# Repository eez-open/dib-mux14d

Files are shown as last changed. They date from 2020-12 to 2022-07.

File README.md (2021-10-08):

### Ownership and License
The contributors are listed in CONTRIB.TXT.

Licenses | OSHWA UID
--|--
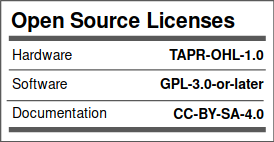
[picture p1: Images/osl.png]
osl
 | OSHW-HR000010 (https://certification.oshwa.org/hr000010.html)

### Overview

The EEZ DIB MUX14D module features two 7:1 reed relay 2-wire multiplexer that can be connect together to make single 14:1 multiplexer. 

### Feature list

* On-board STM32F030C6T6 or STM32F031C4T6 MCU 
* 2 x 16-pin dual row 3.81 mm connectors
* 2 x ADIB connectors (10-pin 2 mm), ADIB ID=002
* Dual 2-wire 7:1 reed relay 2-line multiplexer 
* On-board +3.3 V LDO
* Firmware download via UART
* Optional SWD for debugging
* I2C EEPROM for storing board specific parameters
* Dimensions: 131 x 95 mm, 2-layer PCB

### r1B2 prototype

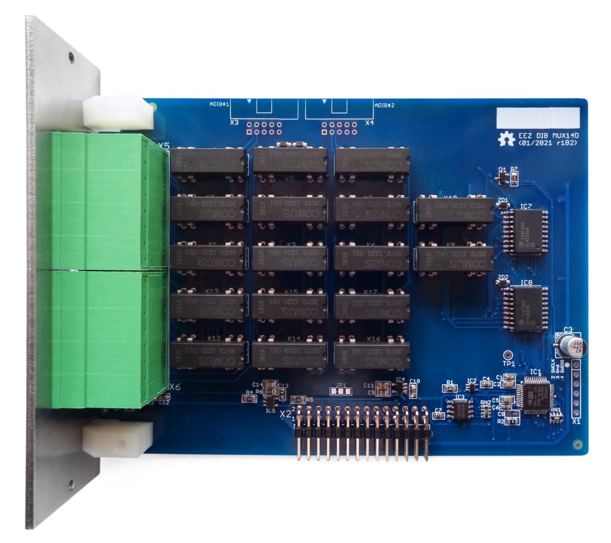
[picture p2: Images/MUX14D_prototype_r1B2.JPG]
prototype


### Firmware repository

https://github.com/eez-open/dib-mux14d-fw  
The firmware download procedure is described in [Chapter 13.2]((https://www.envox.eu/eez-bench-box-3/bb3-user-manual/13-firmware-upgrade/#bb3_man_module_upgrade) of the User Manual.

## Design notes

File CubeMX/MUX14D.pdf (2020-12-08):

## MUX14D Project Configuration Report

# 1. Description

## 1.1. Project

Project Name | MUX14D
Board Name | custom
Generated with: | STM32CubeMX 5.6.1
Date | 12/07/2020

## 1.2. MCU

MCU Series | STM32F0
MCU Line | STM32F0x0 Value Line
MCU name | STM32F030C6Tx
MCU Package | LQFP48
MCU Pin number | 48

# 2. Pinout Configuration

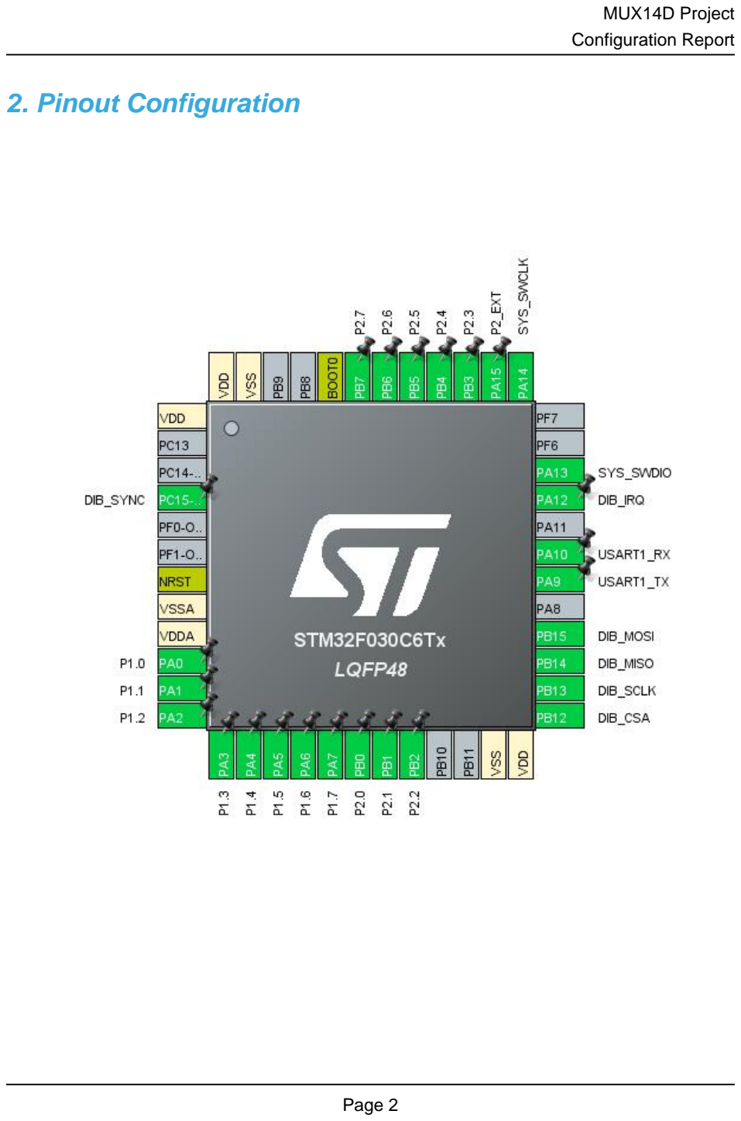
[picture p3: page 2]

# 3. Pins Configuration

Pin Number LQFP48 | Pin Name (function after reset) | Pin Type | Alternate Function(s) | Label
1 | VDD | Power
4 | PC15-OSC32_OUT * | I/O | GPIO_Input | DIB_SYNC
7 | NRST | Reset
8 | VSSA | Power
9 | VDDA | Power
10 | PA0 * | I/O | GPIO_Output | P1.0
11 | PA1 * | I/O | GPIO_Output | P1.1
12 | PA2 * | I/O | GPIO_Output | P1.2
13 | PA3 * | I/O | GPIO_Output | P1.3
14 | PA4 * | I/O | GPIO_Output | P1.4
15 | PA5 * | I/O | GPIO_Output | P1.5
16 | PA6 * | I/O | GPIO_Output | P1.6
17 | PA7 * | I/O | GPIO_Output | P1.7
18 | PB0 * | I/O | GPIO_Output | P2.0
19 | PB1 * | I/O | GPIO_Output | P2.1
20 | PB2 * | I/O | GPIO_Output | P2.2
23 | VSS | Power
24 | VDD | Power
25 | PB12 | I/O | SPI1_NSS | DIB_CSA
26 | PB13 | I/O | SPI1_SCK | DIB_SCLK
27 | PB14 | I/O | SPI1_MISO | DIB_MISO
28 | PB15 | I/O | SPI1_MOSI | DIB_MOSI
30 | PA9 | I/O | USART1_TX
31 | PA10 | I/O | USART1_RX
33 | PA12 * | I/O | GPIO_Output | DIB_IRQ
34 | PA13 | I/O | SYS_SWDIO
37 | PA14 | I/O | SYS_SWCLK
38 | PA15 * | I/O | GPIO_Output | P2_EXT
39 | PB3 * | I/O | GPIO_Output | P2.3
40 | PB4 * | I/O | GPIO_Output | P2.4
41 | PB5 * | I/O | GPIO_Output | P2.5
42 | PB6 * | I/O | GPIO_Output | P2.6
43 | PB7 * | I/O | GPIO_Output | P2.7
44 | BOOT0 | Boot
47 | VSS | Power
48 | VDD | Power

## * The pin is affected with an I/O function

# 4. Clock Tree Configuration

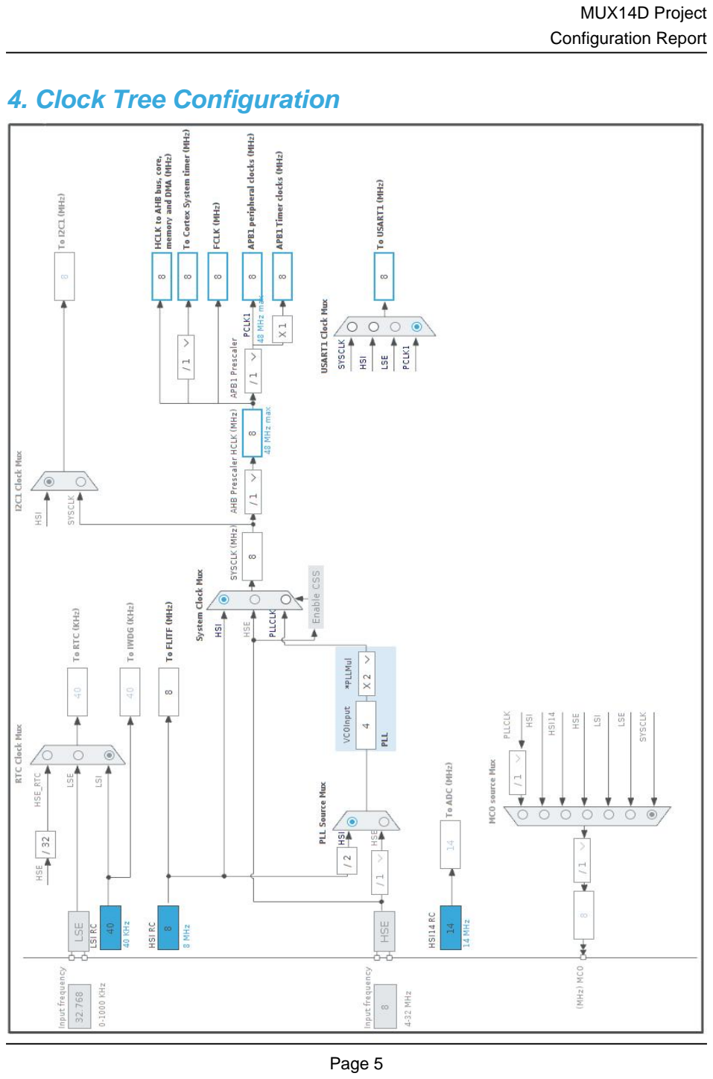
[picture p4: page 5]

# 5. Software Project

## 5.1. Project Settings

Name | Value
Project Name | MUX14D
Project Folder | /home/denis/BACKUP/EEZ/Digital control/MCU/STM32/Projects/MUX14D
Toolchain / IDE | EWARM V8.32
Firmware Package Name and Version | STM32Cube FW_F0 V1.11.0

## 5.2. Code Generation Settings

Name | Value
STM32Cube MCU packages and embedded software | Copy all used libraries into the project folder
Generate peripheral initialization as a pair of '.c/.h' files | No
Backup previously generated files when re-generating | No
Delete previously generated files when not re-generated | Yes
Set all free pins as analog (to optimize the power consumption) | No

# 6. Power Consumption Calculator report

### 6.1. Microcontroller Selection

Series | STM32F0
Line | STM32F0x0 Value Line
MCU | STM32F030C6Tx
Datasheet | 024849_Rev2

### 6.2. Parameter Selection

Temperature | 25
Vdd | 3.6

### 6.3. Battery Selection

Battery | Li-SOCL2(A3400)
Capacity | 3400.0 mAh
Self Discharge | 0.08 %/month
Nominal Voltage | 3.6 V
Max Cont Current | 100.0 mA
Max Pulse Current | 200.0 mA
Cells in series | 1
Cells in parallel | 1

## 6.4. Sequence

Step | Step1 | Step2
Mode | RUN | STOP
Vdd | 3.6 | 3.6
Voltage Source | Battery | Battery
Range | No Scale | No Scale
Fetch Type | FLASH | n/a
CPU Frequency | 48 MHz | 0 Hz
Clock Configuration | HSE PLL All IPs ON | Regulator_LP
Clock Source Frequency | 8 MHz | 0 Hz

### Peripherals

Additional Cons. | 0 mA | 0 mA
Average Current | 23.46 mA | 7.9 µA
Duration | 0.1 ms | 0.9 ms
DMIPS | 0.0 | 0.0
Ta Max | 100.36 | 105
Category | In DS Table | In DS Table

## 6.5. RESULTS

Sequence Time | 1 ms | Average Current | 2.35 mA
Battery Life | 1 month, 29 days, 16 hours | Average DMIPS | 0.0 DMIPS

## 6.6. Chart

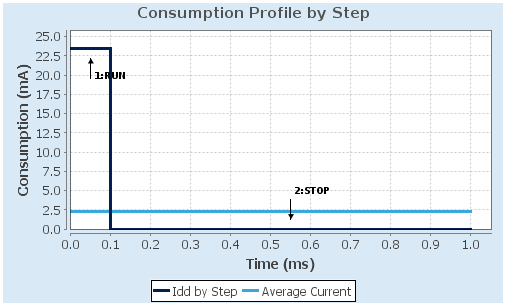
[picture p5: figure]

# 7. IPs and Middleware Configuration

# 7.1. CRC

## mode: Activated 7.1.1. Parameter Settings:

### Basic Parameters:

Default Polynomial State | Enable
Default Init Value State | Enable

### Advanced Parameters:

Input Data Inversion Mode | None
Output Data Inversion Mode | Disable
Input Data Format | Bytes

# 7.2. GPIO

# 7.3. SPI1

## Mode: Full-Duplex Slave Hardware NSS Signal: Hardware NSS Input Signal 7.3.1. Parameter Settings:

### Basic Parameters:

Frame Format | Motorola
Data Size | 4 Bits
First Bit | MSB First

### Clock Parameters:

Clock Polarity (CPOL) | Low
Clock Phase (CPHA) | 1 Edge

### Advanced Parameters:

CRC Calculation | Disabled
NSS Signal Type | Input Hardware

# 7.4. SYS

## mode: Debug Serial Wire Timebase Source: SysTick

# 7.5. USART1

## Mode: Asynchronous 7.5.1. Parameter Settings:

### Basic Parameters:

Baud Rate | 38400
Word Length | 8 Bits (including Parity)
Parity | None
Stop Bits | 1

### Advanced Parameters:

Data Direction | Receive and Transmit
Over Sampling | 16 Samples
Single Sample | Disable

### Advanced Features:

Auto Baudrate | Disable
TX Pin Active Level Inversion | Disable
RX Pin Active Level Inversion | Disable
Data Inversion | Disable
TX and RX Pins Swapping | Disable
Overrun | Enable
DMA on RX Error | Enable
MSB First | Disable

### * User modified value

# 8. System Configuration

# 8.1. GPIO configuration

IP | Pin | Signal | GPIO mode | GPIO pull/up pull down | Max Speed | User Label
SPI1 | PB12 | SPI1_NSS | Alternate Function Push Pull | No pull-up and no pull-down | High * | DIB_CSA
| PB13 | SPI1_SCK | Alternate Function Push Pull | No pull-up and no pull-down | High * | DIB_SCLK
| PB14 | SPI1_MISO | Alternate Function Push Pull | No pull-up and no pull-down | High * | DIB_MISO
| PB15 | SPI1_MOSI | Alternate Function Push Pull | No pull-up and no pull-down | High * | DIB_MOSI
SYS | PA13 | SYS_SWDIO | n/a | n/a | n/a
| PA14 | SYS_SWCLK | n/a | n/a | n/a
USART1 | PA9 | USART1_TX | Alternate Function Push Pull | No pull-up and no pull-down | High *
| PA10 | USART1_RX | Alternate Function Push Pull | No pull-up and no pull-down | High *
| OSC32_OU T | GPIO_Input | Input mode | No pull-up and no pull-down | n/a | DIB_SYNC
| PA0 | GPIO_Output | Output Push Pull | No pull-up and no pull-down | Low | P1.0
| PA1 | GPIO_Output | Output Push Pull | No pull-up and no pull-down | Low | P1.1
| PA2 | GPIO_Output | Output Push Pull | No pull-up and no pull-down | Low | P1.2
| PA3 | GPIO_Output | Output Push Pull | No pull-up and no pull-down | Low | P1.3
| PA4 | GPIO_Output | Output Push Pull | No pull-up and no pull-down | Low | P1.4
| PA5 | GPIO_Output | Output Push Pull | No pull-up and no pull-down | Low | P1.5
| PA6 | GPIO_Output | Output Push Pull | No pull-up and no pull-down | Low | P1.6
| PA7 | GPIO_Output | Output Push Pull | No pull-up and no pull-down | Low | P1.7
| PB0 | GPIO_Output | Output Push Pull | No pull-up and no pull-down | Low | P2.0
| PB1 | GPIO_Output | Output Push Pull | No pull-up and no pull-down | Low | P2.1
| PB2 | GPIO_Output | Output Push Pull | No pull-up and no pull-down | Low | P2.2
| PA12 | GPIO_Output | Output Push Pull | No pull-up and no pull-down | Low | DIB_IRQ
| PA15 | GPIO_Output | Output Push Pull | No pull-up and no pull-down | Low | P2_EXT
| PB3 | GPIO_Output | Output Push Pull | No pull-up and no pull-down | Low | P2.3
| PB4 | GPIO_Output | Output Push Pull | No pull-up and no pull-down | Low | P2.4
| PB5 | GPIO_Output | Output Push Pull | No pull-up and no pull-down | Low | P2.5
| PB6 | GPIO_Output | Output Push Pull | No pull-up and no pull-down | Low | P2.6
| PB7 | GPIO_Output | Output Push Pull | No pull-up and no pull-down | Low | P2.7
GPIO | PC15-

# 8.2. DMA configuration

DMA request | Stream | Direction | Priority
SPI1_RX | DMA1_Channel2 | Peripheral To Memory | Low
SPI1_TX | DMA1_Channel3 | Memory To Peripheral | Low

## SPI1_RX: DMA1_Channel2 DMA request Settings:

Mode: | Normal
Peripheral Increment: | Disable
Memory Increment: | Enable *
Peripheral Data Width: | Byte
Memory Data Width: | Byte

## SPI1_TX: DMA1_Channel3 DMA request Settings:

Mode: | Normal
Peripheral Increment: | Disable
Memory Increment: | Enable *
Peripheral Data Width: | Byte
Memory Data Width: | Byte

# 8.3. NVIC configuration

Interrupt Table | Enable | Preenmption Priority | SubPriority
Non maskable interrupt | true | 0 | 0
Hard fault interrupt | true | 0 | 0
System service call via SWI instruction | true | 0 | 0
Pendable request for system service | true | 0 | 0
System tick timer | true | 0 | 0
DMA1 channel 2 and 3 interrupts | true | 0 | 0
Flash global interrupt | unused
RCC global interrupt | unused
SPI1 global interrupt | unused
USART1 global interrupt | unused

### * User modified value

# 9. Predefined Views - Category view : Current

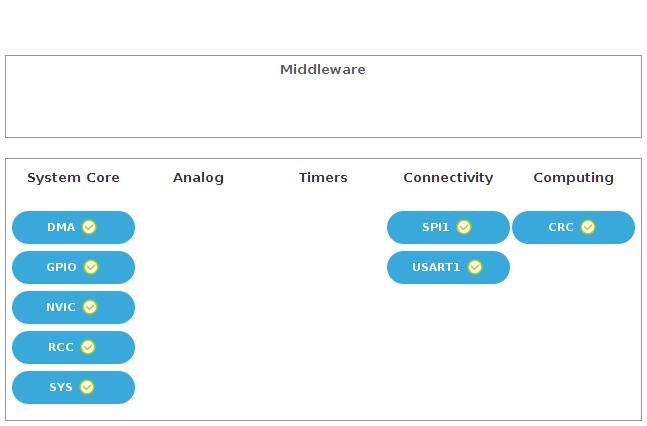
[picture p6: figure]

# 10. Software Pack Report

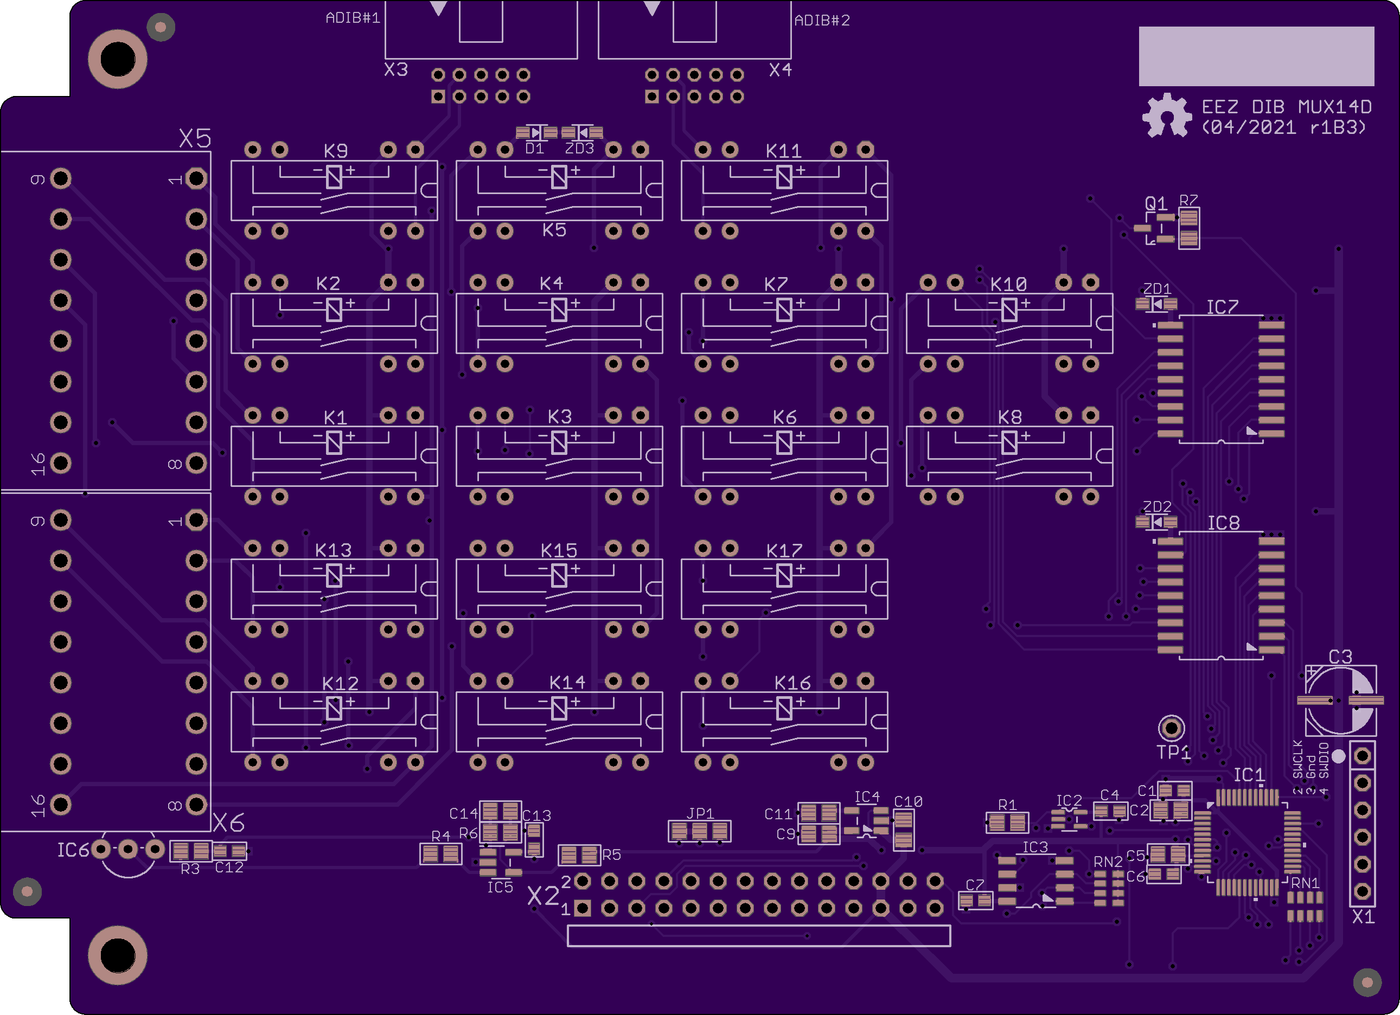
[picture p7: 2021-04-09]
Images/EEZ_DIB_MUX14D_PCB_top.png

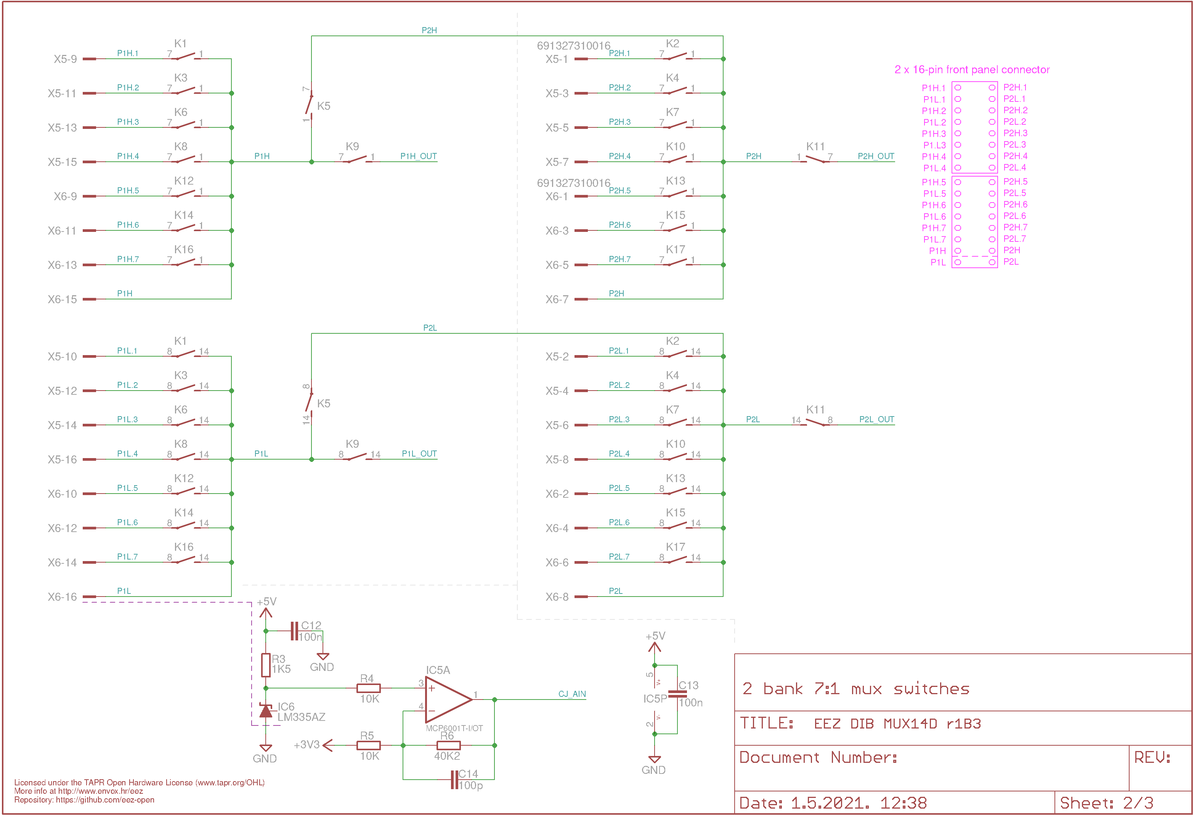
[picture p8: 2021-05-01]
EEZ DIB MUX14D r1B3 Sheet2of3.png

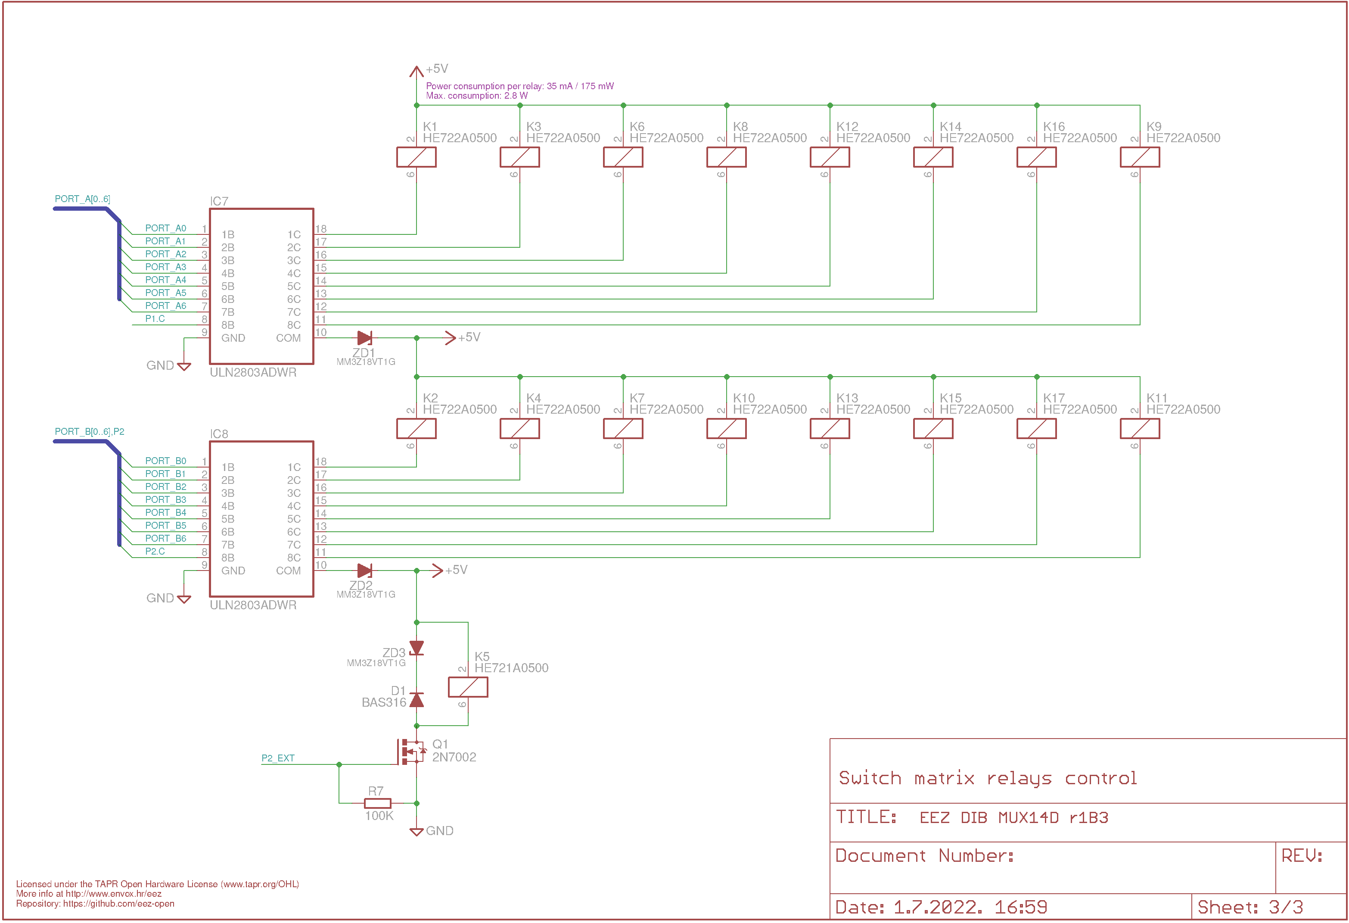
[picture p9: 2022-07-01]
EEZ DIB MUX14D r1B3 Sheet3of3.png

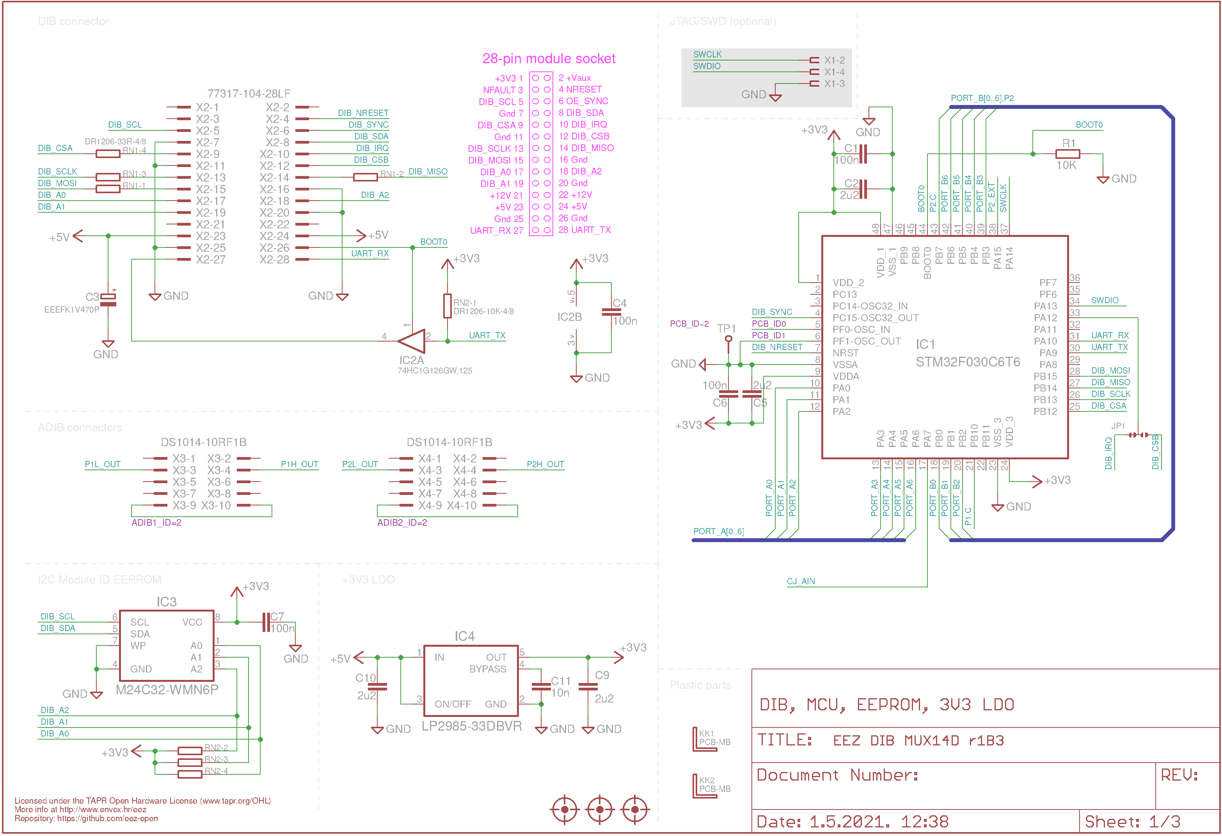
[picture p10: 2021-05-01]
EEZ DIB MUX14D r1B3 Sheet1of3.png

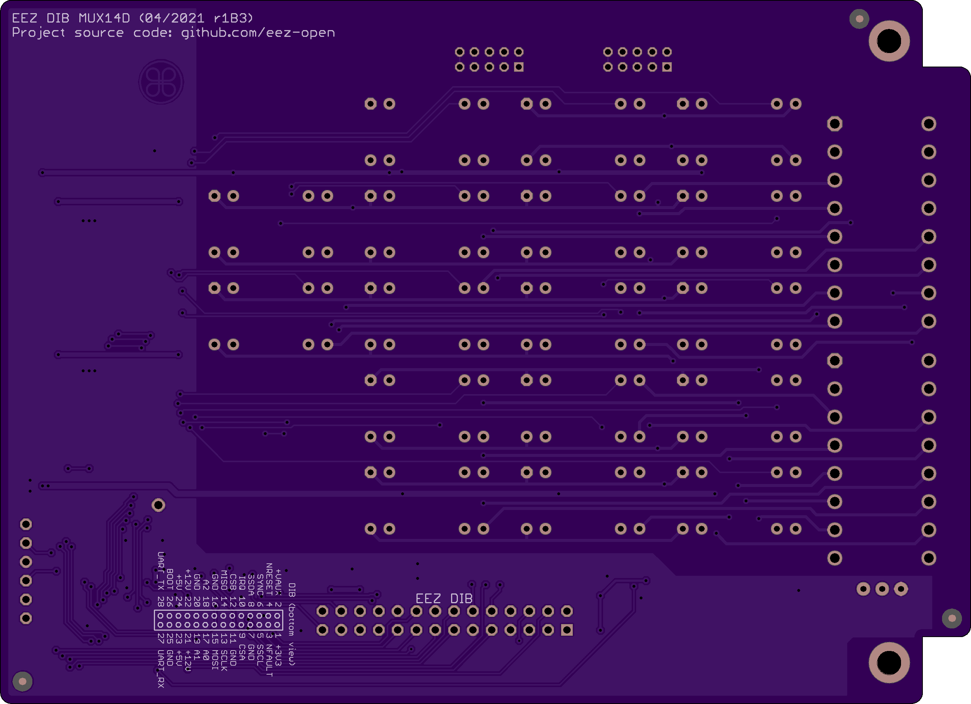
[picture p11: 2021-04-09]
Images/EEZ_DIB_MUX14D_PCB_bottom.png

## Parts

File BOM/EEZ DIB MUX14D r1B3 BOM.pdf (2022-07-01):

EEZ DIB MUX14D BOM (r1B3, 2022-07-01) Project source code at https://github.com/eez-open/dib-prel6
Farnell / Element14 # Unit price Qty Part name Package Reference designator Code Part Number MOQ € | Digi-Key Unit price Part Number MOQ € | Mouser Unit price Part Number MOQ €
| | 80-C0603C104M4R
VJ0805Y103JXXP W1BC | | 710-885012207122
| | 80-C0805C101K5G
C2, C5, C9, C10 GRM21BR71C225 KA12L | | 80-C0805C225M4R ECLR
| | 667-EEE-FK1V470P
1 | 6 100n | 0603 | 2522597 | 0,011 10 | 490-4774-1-ND | 0,029 100 | 0,007 100
2 | 1 10n | 0805 | C11 | 2896555 | 0,065 10 | 490-7194-1-ND | 0,017 | 10 | 0,036 10
3 | 1 100p | C0G, 0805 | C14 | 2896861 | 0,023 10 | 399-15000-1-ND | 0,019 | 10 | 0,032 10
4 | 4 2u2 | 0805 | 1828829 | 0,198 | 5 | 1276-2954-1-ND | 0,085 | 10 | 0,078 10
5 | 1 EEEFK1V470P | C3 | 9695850 | EEEFK1V470P | 0,344 | 1 | PCE3842CT-ND | 0,312 | 10 | 0,238 10
6 | 1 BAS316 | SOD-323 | D1 | 8734275 | BAS316,115 | 0,193 | 5 | 1727-7370-1-ND | 0,120 | 1 | 771-BAS316-T/R | 0,179 | 1
7 | 1 STM32F030C6T6 | LQFP-48 | IC1 | 2393632 | STM32F030C6T6 | 1,350 | 1 | | 1,360 | 1 | | 1,360 | 1
8 | 1 74HC1G126GW.125 | TSSOP-5 | IC2 | - | | | | 1727-6037-1-ND | 0,360 | 1 | 0,369 | 1
9 | 1 M24C32-WMN6P | SOIC-8 | IC3 | 1224413 | M24C32-WMN6P | 0,212 | 5 | - | | | 0,210 | 1
10 | 1 | SOT-23-5 | IC4 | 1053660 | | 0,610 | 1 | 296-18476-1-ND | 0,540 | 1 | 0,507 | 1
11 | 1 | SOT-23-5 | IC5 | 4974992 | MCP6001T-I/OT | 0,219 | 1 | | 0,200 | 1 | 0,203 | 1
12 | 1 LM335AZ | | IC6 | 1564358 | LM335AZ | 1,780 | 1 | | 1,760 | 1 | 1,740 | 1
13 | 2 ULN2803ADWR | SOIC-18 | IC7, IC8 | 3125103 | ULN2803ADWR | 1,120 | 5 | 296-15777-1-ND | 1,090 | 1 | 1,090 | 1
14 | 17 HE722A0500 | - | HE722A0500 | 4,323 | 10 | 4,300 10
15 | 1 2N7002 | SOT-23 | Q1 | 1713825 | 2N7002K-7 | 0,148 | 5 | 0,126 | 10 | 0,113 10
16 | 3 10K | 0805 | R1, R4, R5 | 9237755 | 0,022 10 | 0,039 | 10 | 0,014 10
17 | 1 1K5 | 0805 | R3 | 2447592 | 0,009 10 | A129751CT-ND | 0,041 | 10 | 0,041 10
18 | 1 40K2 | 0805 | R6 | 2447658 | 0,009 10 | 0,055 | 10 | 0,035 10
19 | 1 100K | 0805 | R7 | 2447551 | 0,010 10 | 0,024 | 10 | 0,040 10
20 | 1 DR1206-33R-4/8 | 1206 resistor array | RN1 | 1770128 | CAY16-330J4LF | 0,069 10 | 0,090 | 1 | 0,085 | 1
21 | 1 DR1206-10K-4/8 | 1206 resistor array | RN2 | 1770137 | CAY16-103J4LF | 0,031 10 | 0,058 | 10 | 0,021 10
C1, C4, C6, C7, C12, C13 | C0603C104K4RAC
| 7081

C0805C101JAGAC
TU
STM32F030C6T 6TR | 511-STM32F030C6T 6
Option: 2849912 STM32F031C4T6 2,510 1 STM32F031C4T6 | 497-13617-ND 2,200 | STM32F031C4T 2,110 1 6
| | 771-HC1G126GW125
| | 511-M24C32-WMN6P
| | 595-LP2985-33DBVR
MCP6001T-I/OT or TLV9001IDBVR | MCP6001T-I/OTCT-ND | 579-MCP6001T-E/OT
| PB-ND | 926-LM335AZ/NOPB
| | 595-ULN2803ADWR
| | 934-HE722A0500
| T2N7002AKLMC T-ND | 757-T2N7002AKLM
| 311-10.0KCRCT-ND | 603-RC0805FR-0710KL
MCWR08X1501FT L | | 279-CRGCQ0805F1K 5
| 541-40.2KCCT-ND | 791-WR08X4022FTL
MCWR08X1003FT L | RMCF0805FT10 0KCT-ND | 71-CRCW0805100K FKEAC
| CAY16-330J4LFCT-ND | 652-CAY16-330J4LF
| CAY16-103J4LFCT-ND | 652-CAY16-103J4LF
LP2985-33DBVR | LP2985A- 33DBVTE4 .
THT; TO-92 | LM335AZNS/NO
THT; reed relay | K1, K2, K3, K4, K5, K6, K7, K8, K9, K10, K11, K12, K13, K14, K15, K16, K17

RC0805FR-0710KL

MCWR08X4022FT
L

# Qty Part name | RS Components | TME | Price calculation for 1 set

Unit price Code Part Number MOQ € | Unit price Code / Part Number MOQ € | THT SMD | | Line Cost €

1 6 100n

2 1 10n

3 1 100p

4 4 2u2

5 1 EEEFK1V470P

6 1 BAS316
7 1 STM32F030C6T6

8 1 74HC1G126GW.125

9 1 M24C32-WMN6P

10 1

11 1

12 1 LM335AZ

13 2 ULN2803ADWR

14 17 HE722A0500

15 1 2N7002

16 3 10K

17 1 1K5

18 1 40K2

19 1 100K

20 1 DR1206-33R-4/8

21 1 DR1206-10K-4/8

Option:
STM32F031C4T6

LP2985-33DBVR

MCP6001T-I/OT or
TLV9001IDBVR
393-6952 | 0,069 25 | CL10B104KA8NNNC | 0,098 100 | 6 | Mouser | 0,007 € | 6 | 0,042
464-6672 | 0,026 50 | CC0805KRX7R9103 | 0,027 100 | 1 | Digikey | 0,017 € | 1 | 0,017
461-3997 | 0,030 50 | CL21C101JBANNNC | 0,026 100 | 1 | Digikey | 0,019 € | 1 | 0,019
766-1031 | 0,069 100 | CL21B225KOFNNNG | 0,071 100 | 4 | RS | 0,069 € | 4 | 0,276
537-0657 EEEFK1V470P | 0,394 | 5 | EEEFK1V470P | 0,130 | 5 | 1 | TME | 0,130 € | 1 | 0,130
397-2914 BAS316,115 | 0,122 50 | BAS316,115 | 0,026 25 | 1 | TME | 0,026 € | 1 | 0,026
192-0993 | 0,972 | 5 | STM32F030C6T6 | 0,940 | 4 | 1 | TME | 0,940 € | 1 | 0,940
192-1080 | 2,152 | 5 | STM32F031C4T6 | 2,050 | 1
813-9282 | 0,024 100 | 74HC1G126GW.125 | 0,062 10 | 1 | RS | 0,024 € | 1 | 0,024
686-2453 | 0,180 25 | M24C32-WMN6P | 0,165 | 3 | 1 | TME | 0,165 € | 1 | 0,165
660-6733 LP2985-33DBVT | 0,737 | 1 | LP2985-33DBVR | 0,362 | 1 | 1 | TME | 0,362 € | 1 | 0,362
698-9041 MCP6001T-I/OT | 0,230 | 1 | MCP6001T-I/OT | 0,254 | 3 | 1 | Digikey | 0,200 € | 1 | 0,200
LM335AZ | 1,188 | 1 | LM335AZ | 0,850 | 1 | 1 | TME | 0,850 € | 1 | 0,850
646-6311 ULN2803ADW | 1,336 | 5 | ULN2803ADWR | 0,874 | 1 | 2 | TME | 0,874 € | 2 | 1,748
- | - | 17 | Mouser | 4,300 € 17 | 73,100
671-0312 2N7002 | 1,250 20 | 2N7002LT1G | 0,019 25 | 1 | TME | 0,019 € | 1 | 0,019
125-1189 CRG0805F10K | 0,002 100 | RC0805FR-0710K | 0,022 100 | 3 | RS | 0,002 € | 3 | 0,006
223-0449 CRG0805F1K5 | 0,027 50 | 805S8F1501T5E | 0,014 100 | 1 | Farnell | 0,009 € | 1 | 0,009
679-1395 | 0,004 50 | 0805S8F4022T5E | 0,014 100 | 1 | RS | 0,004 € | 1 | 0,004
223-0691 CRG0805F100K | 0,028 50 | 0805S8F1003T5E | 0,015 100 | 1 | Farnell | 0,010 € | 1 | 0,010
522-5670 CAY16-330J4LF | 0,004 50 | 4D03WGJ0330T | 0,009 100 | 1 | RS | 0,004 € | 1 | 0,004
522-5585 CAY16-103J4LF | 0,012 50 | 4D03WGJ0103T | 0,011 100 | 1 | TME | 0,011 € | 1 | 0,011

Best
Supplier

Lowest
unit price
€

Order
Qty

VJ0603Y104KXJ
AT
08055C103KAT
2A
CC0805JRNP09
BN101
CL21B225KAFN
NNF

STM32F030C6T
6TR

STM32F031C4T
6
74HC1G126GW,
125
M24C32-
WMN6P

CRCW080540K
2FKEA

Farnell / Element14 # Qty Part name Package Reference designator Code Part Number MOQ € | Digi-Key Part Number Unit price MOQ € | Mouser Part Number Unit price MOQ Unit price €
| | 649-77317-104-28LF

THT, 10-pin 2mm IDC, right angle

| 732-691327310016-ND
| MM3Z18VT1GO SCT-ND | 863-MM3Z18VT1G
22 | 1 77317-104-28LF | X2 | - | S2111EC-14-ND | 1,030 | 1 | 1,540 | 1
23 | 2 DS1014-10RF1B | X3, X4 | - | 2BHR-10-HUA | 0,650 | 1 | -
24 | 2 691327310016 | X5, X6 | 1793077 | 5,770 | 1 | 7,810 | 1 | 651-1843130 | 9,270 | 1
25 | 3 MM3Z18VT1G | SOD-323 | ZD1, ZD2, ZD3 | 1431193 | MM3Z18VT1G | 0,109 10 | 0,103 | 10 | 0,108 10

Not installed
1 N.C. | | X1

Related parts and accessories
2 PMB-1 | PCB bracket; polyamide | KK1, KK2 | - | - | -
2 M3X4/D7985

2 M3X5/D965B

Custom made components
1 | -
| All prices are net prices (without VAT)

All resistors are 1% 0805 and all capacitors are X7R 0805 if not otherwise specified.

THT, 28-pin 0.1" header right angled

THT, 16-pin 3.81mm terminal block header, male pins

MCD 1,5/ 8-G1-
3,81

Screw; M3x4; cheese head;
Phillips

Module's studs mounting
(bottom), AC/DC mounting
frame (top), 3 x AC/DC
modules mounting
Screw; M3x5; countersunk;
Phillips; black finish

Module's studs mounting
(top), front and rear panel fixing, modules mounting on the front panel

PCB 2-layer 131 x 95
mm

Please note that BOM does not contain ordering number for parts on reels or that which includes re-reeling fee (e.g. Farnell). Take also into account that total cost is higher because min. quantity (MOQ) for many parts is larger then what is needed for single unit.

# Qty Part name | RS Components | TME | Price calculation for 1 set

Code Part Number MOQ € | Code / Part Number Unit price MOQ € | THT SMD | | Line Cost € Unit price

22 1 77317-104-28LF

23 2 DS1014-10RF1B

24 2 691327310016

25 3 MM3Z18VT1G

Not installed
1 N.C.

Related parts and accessories 2 PMB-1
2 M3X4/D7985

2 M3X5/D965B

Custom made components
1 PCB 2-layer 131 x 95
mm

Best
Supplier

Lowest
unit price
€

Order
Qty
- | - | 1 | Digikey | 1,030 € | 1 | 1,030
- | DS1014-10RF1B | 0,220 | 3 | 2 | TME | 0,220 € | 2 | 0,440
191-1724 691327310016 | 7,900 | 1 | - | 2 | Farnell | 5,770 € | 2 | 11,540
802-4574 MM3Z18VT1G | 0,038 200 | MM3Z18VT1G | 0,025 25 | 3 | TME | 0,025 € | 3 | 0,076
23 | 33 | 91,05 €
1 | Farnell | 0,000 € | 1 | 0,000
- | PMB-1 | 0,072 10 | TME | 0,072 € | 2 | 0,145
| M3X4/D7985 | 0,012 100 | TME | 0,012 € | 2 | 0,023
M3X5/D965B | 0,012 100 | TME | 0,012 € | 2 | 0,025

0,19 €

JLCPCB | 4,218 € | 1 | 4,218
| | | 4,22 €
| | Total | 95,46 €

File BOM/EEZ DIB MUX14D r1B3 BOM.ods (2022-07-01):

 |  |  |  |  | Farnell / Element14 |  |  |  | Digi-Key |  |  | Mouser |  |  | RS Components |  |  |  | TME |  |  |  |  | Price calculation for 1 set
# | Qty | Part name | Package | Reference designator | Code | Part Number | Unit price € | MOQ | Part Number | Unit price € | MOQ | Part Number | Unit price € | MOQ | Code | Part Number | Unit price € | MOQ | Code / Part Number | Unit price € | MOQ | THT | SMD | Best Supplier | Lowest unit price € | Order Qty | Line Cost €
1 | 6 | 100n | 0603 | C1, C4, C6, C7, C12, C13 | 2522597 | C0603C104K4RAC7081 | 0,011 | 10 | 490-4774-1-ND | 0,029 | 100 | 80-C0603C104M4R | 0,007 | 100 | 393-6952 | VJ0603Y104KXJAT | 0,069 | 25 | CL10B104KA8NNNC | 0,098 | 100 |  | 6 | Mouser | 0,007 € | 6 | 0,042
2 | 1 | 10n | 0805 | C11 | 2896555 | VJ0805Y103JXXPW1BC | 0,065 | 10 | 490-7194-1-ND | 0,017 | 10 | 710-885012207122 | 0,036 | 10 | 464-6672 | 08055C103KAT2A | 0,026 | 50 | CC0805KRX7R9103 | 0,027 | 100 |  | 1 | Digikey | 0,017 € | 1 | 0,017
3 | 1 | 100p | C0G, 0805 | C14 | 2896861 | C0805C101JAGACTU | 0,023 | 10 | 399-15000-1-ND | 0,019 | 10 | 80-C0805C101K5G | 0,032 | 10 | 461-3997 | CC0805JRNP09BN101 | 0,030 | 50 | CL21C101JBANNNC | 0,026 | 100 |  | 1 | Digikey | 0,019 € | 1 | 0,019
4 | 4 | 2u2 | 0805 | C2, C5, C9, C10 | 1828829 | GRM21BR71C225KA12L | 0,198 | 5 | 1276-2954-1-ND | 0,085 | 10 | 80-C0805C225M4RECLR | 0,078 | 10 | 766-1031 | CL21B225KAFNNNF | 0,069 | 100 | CL21B225KOFNNNG | 0,071 | 100 |  | 4 | RS | 0,069 € | 4 | 0,276
5 | 1 | EEEFK1V470P |  | C3 | 9695850 | EEEFK1V470P | 0,344 | 1 | PCE3842CT-ND | 0,312 | 10 | 667-EEE-FK1V470P | 0,238 | 10 | 537-0657 | EEEFK1V470P | 0,394 | 5 | EEEFK1V470P | 0,130 | 5 |  | 1 | TME | 0,130 € | 1 | 0,130
6 | 1 | BAS316 | SOD-323 | D1 | 8734275 | BAS316,115 | 0,193 | 5 | 1727-7370-1-ND | 0,120 | 1 | 771-BAS316-T/R | 0,179 | 1 | 397-2914 | BAS316,115 | 0,122 | 50 | BAS316,115 | 0,026 | 25 |  | 1 | TME | 0,026 € | 1 | 0,026
7 | 1 | STM32F030C6T6 | LQFP-48 | IC1 | 2393632 | STM32F030C6T6 | 1,350 | 1 | STM32F030C6T6TR | 1,360 | 1 | 511-STM32F030C6T6 | 1,360 | 1 | 192-0993 | STM32F030C6T6TR | 0,972 | 5 | STM32F030C6T6 | 0,940 | 4 |  | 1 | TME | 0,940 € | 1 | 0,940
 |  | Option: STM32F031C4T6 |  |  | 2849912 | STM32F031C4T6 | 2,510 | 1 | 497-13617-ND | 2,200 |  | STM32F031C4T6 | 2,110 | 1 | 192-1080 | STM32F031C4T6 | 2,152 | 5 | STM32F031C4T6 | 2,050 | 1
8 | 1 | 74HC1G126GW.125 | TSSOP-5 | IC2 | - |  |  |  | 1727-6037-1-ND | 0,360 | 1 | 771-HC1G126GW125 | 0,369 | 1 | 813-9282 | 74HC1G126GW,125 | 0,024 | 100 | 74HC1G126GW.125 | 0,062 | 10 |  | 1 | RS | 0,024 € | 1 | 0,024
9 | 1 | M24C32-WMN6P | SOIC-8 | IC3 | 1224413 | M24C32-WMN6P | 0,212 | 5 | - |  |  | 511-M24C32-WMN6P | 0,210 | 1 | 686-2453 | M24C32-WMN6P | 0,180 | 25 | M24C32-WMN6P | 0,165 | 3 |  | 1 | TME | 0,165 € | 1 | 0,165
10 | 1 | LP2985-33DBVR | SOT-23-5 | IC4 | 1053660 | LP2985A-33DBVTE4 . | 0,610 | 1 | 296-18476-1-ND | 0,540 | 1 | 595-LP2985-33DBVR | 0,507 | 1 | 660-6733 | LP2985-33DBVT | 0,737 | 1 | LP2985-33DBVR | 0,362 | 1 |  | 1 | TME | 0,362 € | 1 | 0,362
11 | 1 | MCP6001T-I/OT or TLV9001IDBVR | SOT-23-5 | IC5 | 4974992 | MCP6001T-I/OT | 0,219 | 1 | MCP6001T-I/OTCT-ND | 0,200 | 1 | 579-MCP6001T-E/OT | 0,203 | 1 | 698-9041 | MCP6001T-I/OT | 0,230 | 1 | MCP6001T-I/OT | 0,254 | 3 |  | 1 | Digikey | 0,200 € | 1 | 0,200
12 | 1 | LM335AZ | THT; TO-92 | IC6 | 1564358 | LM335AZ | 1,780 | 1 | LM335AZNS/NOPB-ND | 1,760 | 1 | 926-LM335AZ/NOPB | 1,740 | 1 |  | LM335AZ | 1,188 | 1 | LM335AZ | 0,850 | 1 | 1 |  | TME | 0,850 € | 1 | 0,850
13 | 2 | ULN2803ADWR | SOIC-18 | IC7, IC8 | 3125103 | ULN2803ADWR | 1,120 | 5 | 296-15777-1-ND | 1,090 | 1 | 595-ULN2803ADWR | 1,090 | 1 | 646-6311 | ULN2803ADW | 1,336 | 5 | ULN2803ADWR | 0,874 | 1 |  | 2 | TME | 0,874 € | 2 | 1,748
14 | 17 | HE722A0500 | THT; reed relay | K1, K2, K3, K4, K5, K6, K7, K8, K9, K10, K11, K12, K13, K14, K15, K16, K17 | - |  |  |  | HE722A0500 | 4,323 | 10 | 934-HE722A0500 | 4,300 | 10 | - |  |  |  | - |  |  | 17 |  | Mouser | 4,300 € | 17 | 73,100
15 | 1 | 2N7002 | SOT-23 | Q1 | 1713825 | 2N7002K-7 | 0,148 | 5 | T2N7002AKLMCT-ND | 0,126 | 10 | 757-T2N7002AKLM | 0,113 | 10 | 671-0312 | 2N7002 | 1,250 | 20 | 2N7002LT1G | 0,019 | 25 |  | 1 | TME | 0,019 € | 1 | 0,019
16 | 3 | 10K | 0805 | R1, R4, R5 | 9237755 | RC0805FR-0710KL | 0,022 | 10 | 311-10.0KCRCT-ND | 0,039 | 10 | 603-RC0805FR-0710KL | 0,014 | 10 | 125-1189 | CRG0805F10K | 0,002 | 100 | RC0805FR-0710K | 0,022 | 100 |  | 3 | RS | 0,002 € | 3 | 0,006
17 | 1 | 1K5 | 0805 | R3 | 2447592 | MCWR08X1501FTL | 0,009 | 10 | A129751CT-ND | 0,041 | 10 | 279-CRGCQ0805F1K5 | 0,041 | 10 | 223-0449 | CRG0805F1K5 | 0,027 | 50 | 805S8F1501T5E | 0,014 | 100 |  | 1 | Farnell | 0,009 € | 1 | 0,009
18 | 1 | 40K2 | 0805 | R6 | 2447658 | MCWR08X4022FTL | 0,009 | 10 | 541-40.2KCCT-ND | 0,055 | 10 | 791-WR08X4022FTL | 0,035 | 10 | 679-1395 | CRCW080540K2FKEA | 0,004 | 50 | 0805S8F4022T5E | 0,014 | 100 |  | 1 | RS | 0,004 € | 1 | 0,004
19 | 1 | 100K | 0805 | R7 | 2447551 | MCWR08X1003FTL | 0,010 | 10 | RMCF0805FT100KCT-ND | 0,024 | 10 | 71-CRCW0805100KFKEAC | 0,040 | 10 | 223-0691 | CRG0805F100K | 0,028 | 50 | 0805S8F1003T5E | 0,015 | 100 |  | 1 | Farnell | 0,010 € | 1 | 0,010
20 | 1 | DR1206-33R-4/8 | 1206 resistor array | RN1 | 1770128 | CAY16-330J4LF | 0,069 | 10 | CAY16-330J4LFCT-ND | 0,090 | 1 | 652-CAY16-330J4LF | 0,085 | 1 | 522-5670 | CAY16-330J4LF | 0,004 | 50 | 4D03WGJ0330T | 0,009 | 100 |  | 1 | RS | 0,004 € | 1 | 0,004
21 | 1 | DR1206-10K-4/8 | 1206 resistor array | RN2 | 1770137 | CAY16-103J4LF | 0,031 | 10 | CAY16-103J4LFCT-ND | 0,058 | 10 | 652-CAY16-103J4LF | 0,021 | 10 | 522-5585 | CAY16-103J4LF | 0,012 | 50 | 4D03WGJ0103T | 0,011 | 100 |  | 1 | TME | 0,011 € | 1 | 0,011
22 | 1 | 77317-104-28LF | THT, 28-pin 0.1" header right angled | X2 | - |  |  |  | S2111EC-14-ND | 1,030 | 1 | 649-77317-104-28LF | 1,540 | 1 | - |  |  |  | - |  |  | 1 |  | Digikey | 1,030 € | 1 | 1,030
23 | 2 | DS1014-10RF1B | THT, 10-pin 2mm IDC, right angle | X3, X4 | - |  |  |  | 2BHR-10-HUA | 0,650 | 1 | - |  |  | - |  |  |  | DS1014-10RF1B | 0,220 | 3 | 2 |  | TME | 0,220 € | 2 | 0,440
24 | 2 | 691327310016 | THT, 16-pin 3.81mm terminal block header, male pins | X5, X6 | 1793077 | MCD 1,5/ 8-G1-3,81 | 5,770 | 1 | 732-691327310016-ND | 7,810 | 1 | 651-1843130 | 9,270 | 1 | 191-1724 | 691327310016 | 7,900 | 1 | - |  |  | 2 |  | Farnell | 5,770 € | 2 | 11,540
25 | 3 | MM3Z18VT1G | SOD-323 | ZD1, ZD2, ZD3 | 1431193 | MM3Z18VT1G | 0,109 | 10 | MM3Z18VT1GOSCT-ND | 0,103 | 10 | 863-MM3Z18VT1G | 0,108 | 10 | 802-4574 | MM3Z18VT1G | 0,038 | 200 | MM3Z18VT1G | 0,025 | 25 |  | 3 | TME | 0,025 € | 3 | 0,076
 |  |  |  |  |  |  |  |  |  |  |  |  |  |  |  |  |  |  |  |  |  | 23 | 33 |  |  |  | 91,05 €
 |  | Not installed
 | 1 | N.C. |  | X1 |  |  |  |  |  |  |  |  |  |  |  |  |  |  |  |  |  | 1 |  | Farnell | 0,000 € | 1 | 0,000
 |  | Related parts and accessories
 | 2 | PMB-1 | PCB bracket; polyamide | KK1, KK2 | - |  |  |  | - |  |  | - |  |  | - |  |  |  | PMB-1 | 0,072 | 10 |  |  | TME | 0,072 € | 2 | 0,145
 | 2 | M3X4/D7985 | Screw; M3x4; cheese head; Phillips | Module's studs mounting (bottom), AC/DC mounting frame (top), 3 x AC/DC modules mounting |  |  |  |  |  |  |  |  |  |  |  |  |  |  | M3X4/D7985 | 0,012 | 100 |  |  | TME | 0,012 € | 2 | 0,023
 | 2 | M3X5/D965B | Screw; M3x5; countersunk; Phillips; black finish | Module's studs mounting (top), front and rear panel fixing, modules mounting on the front panel |  |  |  |  |  |  |  |  |  |  |  |  |  |  | M3X5/D965B | 0,012 | 100 |  |  | TME | 0,012 € | 2 | 0,025
 |  |  |  |  |  |  |  |  |  |  |  |  |  |  |  |  |  |  |  |  |  |  |  |  |  |  | 0,19 €
 |  | Custom made components
 | 1 | PCB 2-layer 131 x 95 mm |  | - |  |  |  |  |  |  |  |  |  |  |  |  |  |  |  |  |  |  |  | JLCPCB | 4,218 € | 1 | 4,218
 |  |  |  |  |  |  |  |  |  |  |  |  |  |  |  |  |  |  |  |  |  |  |  |  |  |  | 4,22 €
 |  |  | All prices are net prices (without VAT)
 |  |  |  |  |  |  |  |  |  |  |  |  |  |  |  |  |  |  |  |  |  |  |  |  |  | Total | 95,46 €
 |  |  | Please note that BOM does not contain ordering number for parts on reels or that which includes re-reeling fee (e.g. Farnell). Take also into account that total cost is higher because min. quantity (MOQ) for many parts is larger then what is needed for single unit.
 |  |  | All resistors are 1% 0805 and all capacitors are X7R 0805 if not otherwise specified.

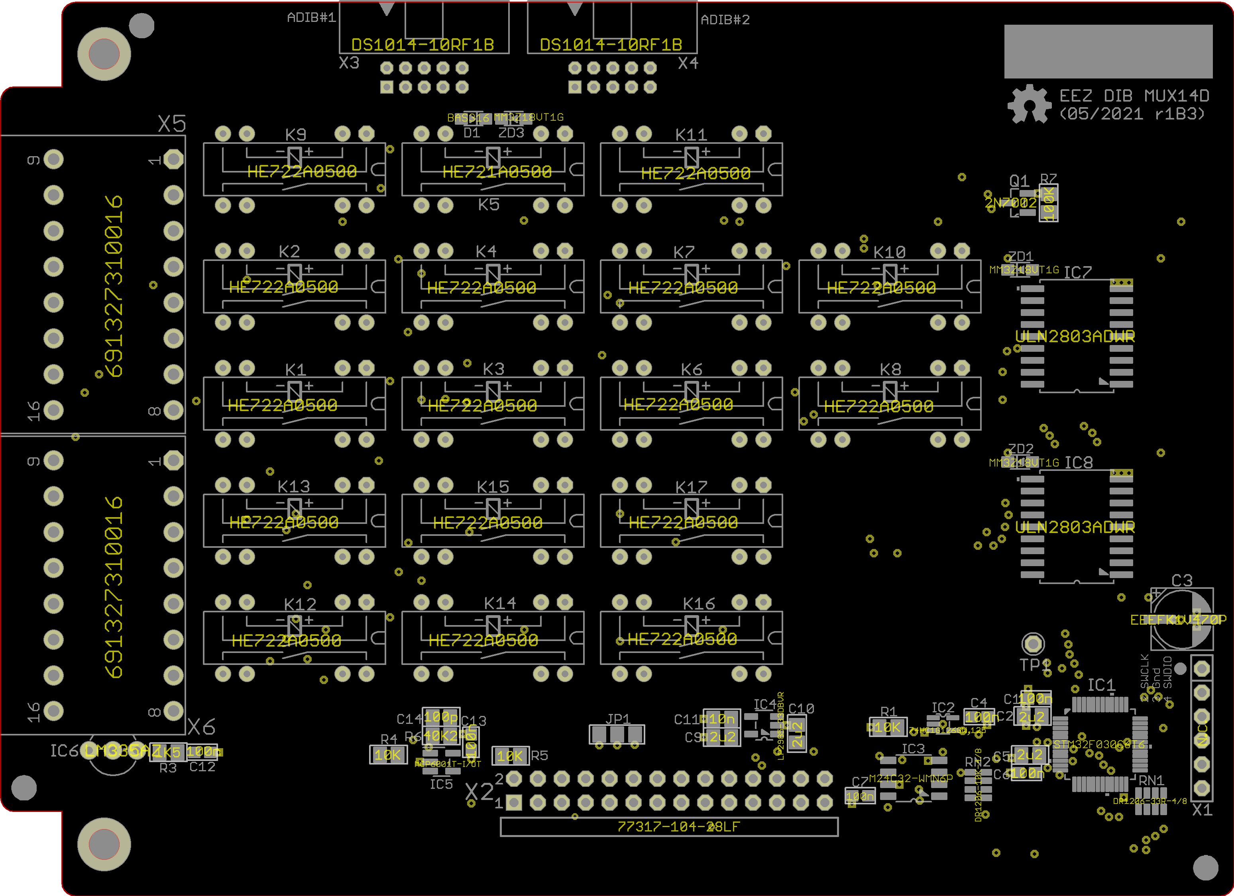
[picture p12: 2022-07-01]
Images/EEZ_DIB_MUX14D_PCB_parts.png

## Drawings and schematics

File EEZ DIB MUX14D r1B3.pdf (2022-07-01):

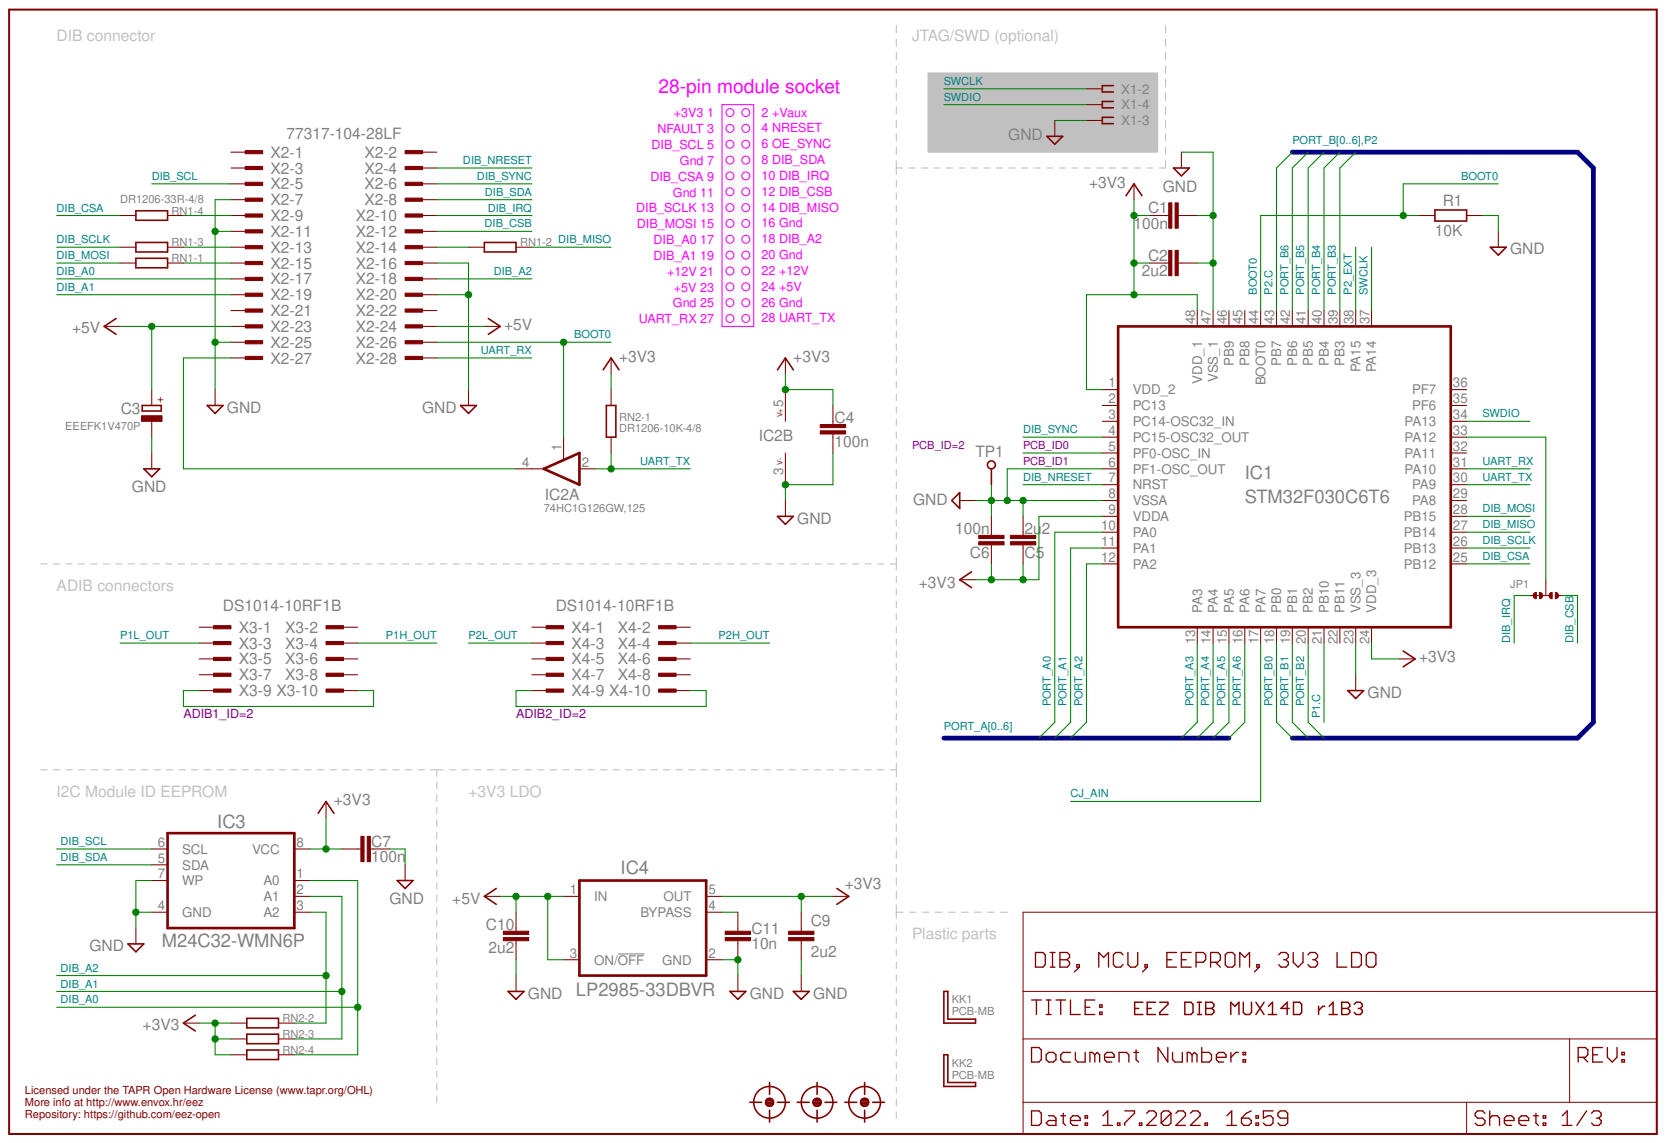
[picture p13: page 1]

Licensed under the TAPR Open Hardware License (www.tapr.org/OHL) Repository: https://github.com/eez-open More info at http://www.envox.hr/eez

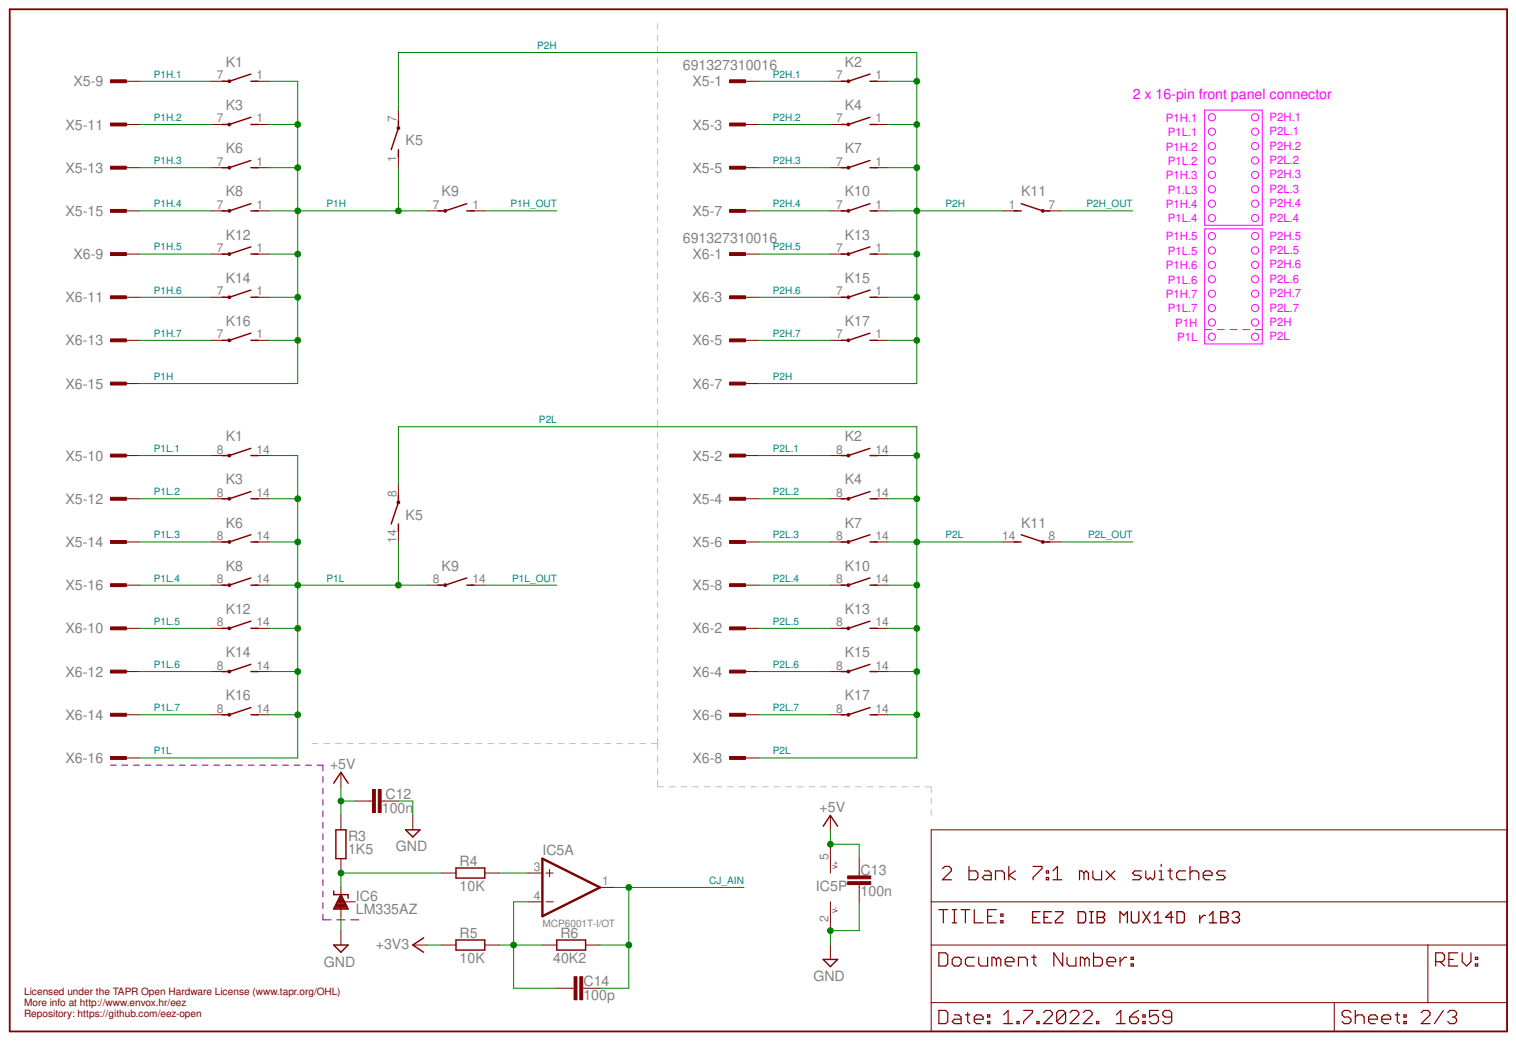
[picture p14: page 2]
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

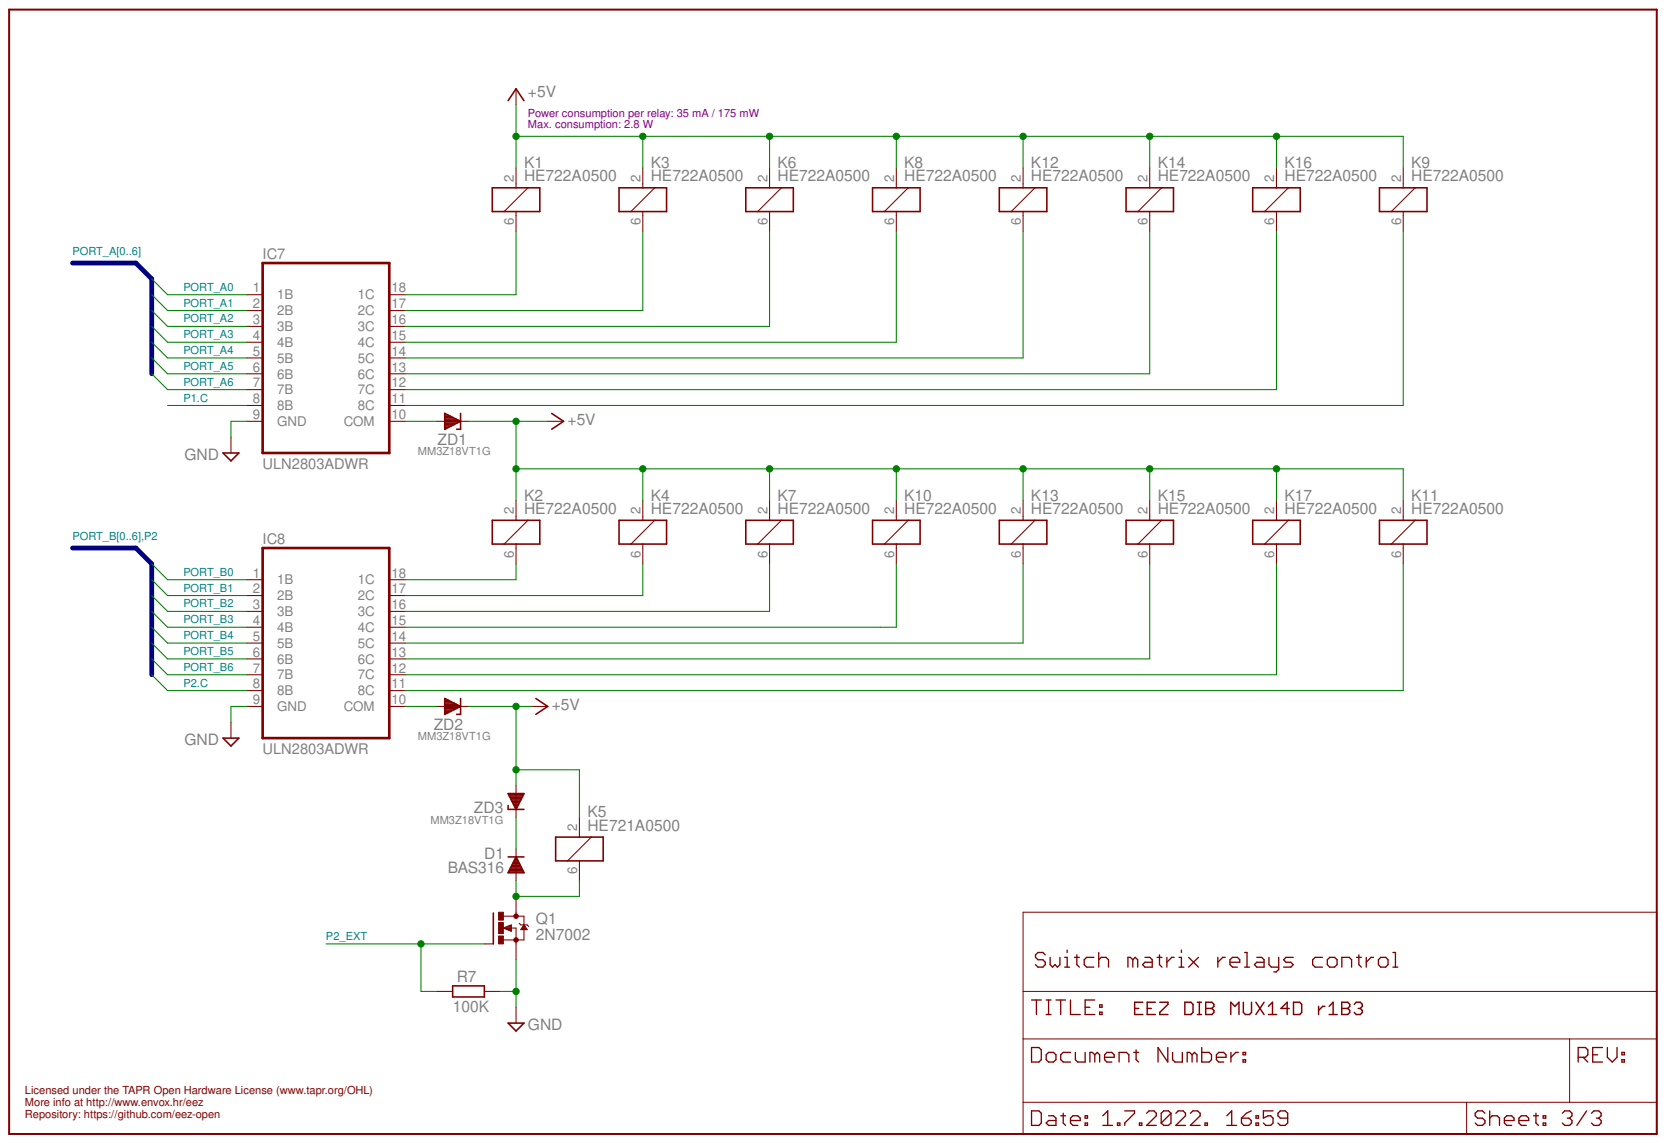
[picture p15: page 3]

Power consumption per relay: 35 mA / 175 mW
Max. consumption: 2.8 W

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

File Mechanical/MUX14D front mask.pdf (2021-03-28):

# MUX14D

H1

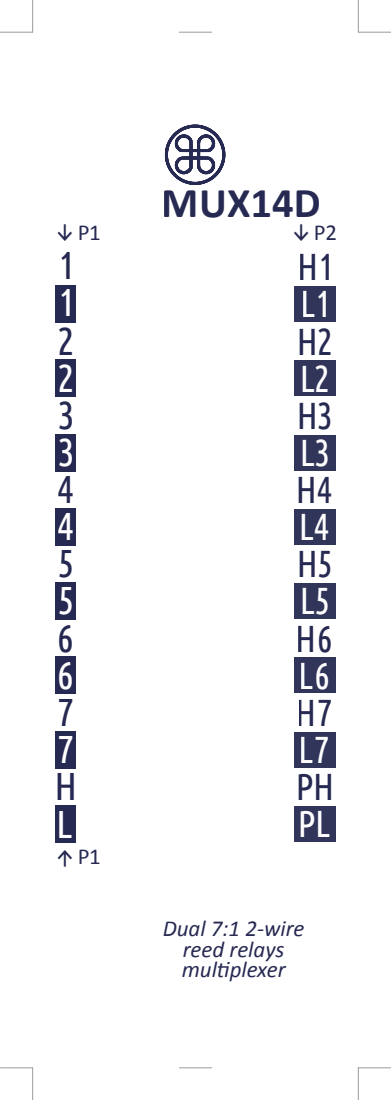
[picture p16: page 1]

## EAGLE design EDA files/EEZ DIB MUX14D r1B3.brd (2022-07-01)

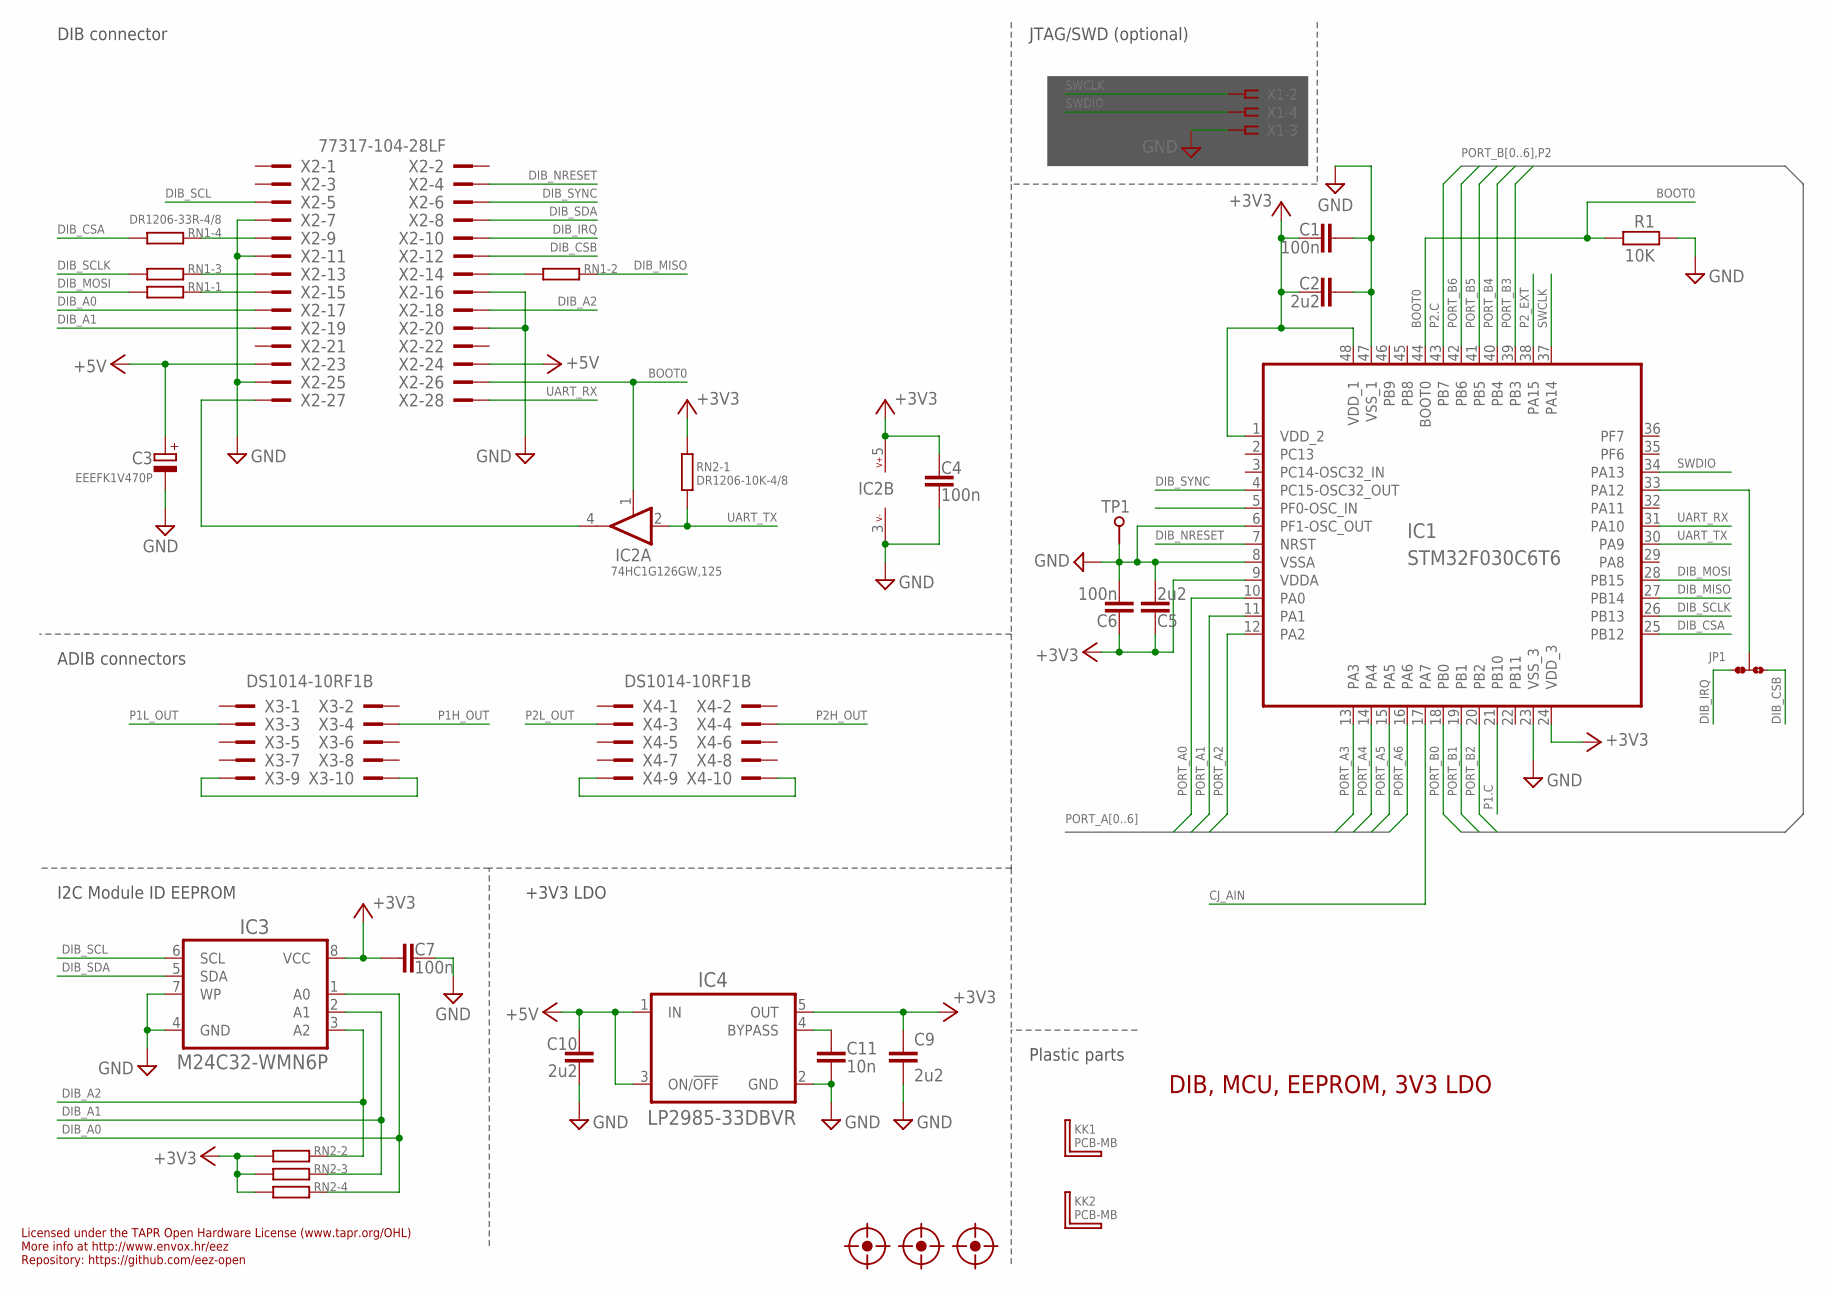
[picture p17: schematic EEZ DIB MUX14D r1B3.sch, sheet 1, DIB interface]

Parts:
C1, C4, C6, C7: 100n; C0603
C2, C5, C9, C10: 2u2; C0805
C3: EEEFK1V470P; CAPAE660X610N
C11: 10n; C0805
FM1, FM2, FM3: FIDUCIAL_2; FIDUCIAL_DUAL
IC1: STM32F030C6T6; LQFP-48
IC2: 74HC1G126GW,125; SOT65P210X110-5N
IC3: M24C32-WMN6P; SOIC127P600X173-8N
IC4: LP2985-33DBVR; SOT95P270X145-5N
JP1: JP3-CUT-0805-ROTATED; JP3-0805-CUT2
KK1, KK2: PCB-MB
R1: 10K; R0805
RN1: DR1206-33R-4/8; CAY16
RN2: DR1206-10K-4/8; CAY16
TP1: PCB_TEST_TABSHIELD; PCB_SHIELD_TAB
X1: N.C.; SSW-106-02-S-S
X2: 77317-104-28LF
X3, X4: DS1014-10RF1B

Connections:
+3V3: C1.2, C2.1, C4.1, C5.2, C6.1, C7.2, C9.1, IC1.1 (VDD_2), IC1.9 (VDDA), IC1.24 (VDD_3), IC1.48 (VDD_1), IC2.5 (V+), IC3.8 (VCC), IC4.5 (OUT), RN2.5 (2), RN2.6 (2), RN2.7 (2), RN2.8 (2); also elsewhere on the board
+5V: C3.1 (+), C10.2, IC4.1 (IN), IC4.3 (ON/!OFF), X2.23, X2.24; also elsewhere on the board
BOOT0: IC1.44 (BOOT0), IC2.1 (EN), R1.2, X2.26
CJ_AIN: IC1.17 (PA7); also elsewhere on the board
DIB_A0: IC3.1 (A0), RN2.4 (1), X2.17
DIB_A1: IC3.2 (A1), RN2.3 (1), X2.19
DIB_A2: IC3.3 (A2), RN2.2 (1), X2.18
DIB_CSA: IC1.25 (PB12), RN1.4 (1)
DIB_CSB: JP1.NO, X2.12
DIB_IRQ: JP1.NC, X2.10
DIB_MISO: IC1.27 (PB14), RN1.2 (1)
DIB_MOSI: IC1.28 (PB15), RN1.1
DIB_NRESET: IC1.7 (NRST), X2.4
DIB_SCL: IC3.6 (SCL), X2.5
DIB_SCLK: IC1.26 (PB13), RN1.3 (1)
DIB_SDA: IC3.5 (SDA), X2.8
DIB_SYNC: IC1.4 (PC15-OSC32_OUT), X2.6
GND: C1.1, C2.2, C3.2 (-), C4.2, C5.1, C6.2, C7.1, C9.2, C10.1, C11.1, IC1.6 (PF1-OSC_OUT), IC1.8 (VSSA), IC1.23 (VSS_3), IC1.47 (VSS_1), IC2.3 (V-), IC3.4 (GND), IC3.7 (WP), IC4.2 (GND), R1.1, TP1.1, X1.3, X2.7, X2.11, X2.16, X2.20, X2.25; also elsewhere on the board
unnamed: X3.9, X3.10
unnamed: X4.9, X4.10
unnamed: RN1.5 (2), X2.9
unnamed: C11.2, IC4.4 (BYPASS)
unnamed: IC2.4 (O), X2.27
unnamed: IC1.33 (PA12), JP1.COM
unnamed: RN1.6 (2), X2.13
unnamed: RN1.7 (2), X2.14
unnamed: RN1.8 (2), X2.15
P1.C: IC1.21 (PB10); also elsewhere on the board
P1H_OUT: X3.4; also elsewhere on the board
P1L_OUT: X3.3; also elsewhere on the board
P2.C: IC1.43 (PB7); also elsewhere on the board
P2H_OUT: X4.4; also elsewhere on the board
P2L_OUT: X4.3; also elsewhere on the board
P2_EXT: IC1.38 (PA15); also elsewhere on the board
PORT_A0: IC1.10 (PA0); also elsewhere on the board
PORT_A1: IC1.11 (PA1); also elsewhere on the board
PORT_A2: IC1.12 (PA2); also elsewhere on the board
PORT_A3: IC1.13 (PA3); also elsewhere on the board
PORT_A4: IC1.14 (PA4); also elsewhere on the board
PORT_A5: IC1.15 (PA5); also elsewhere on the board
PORT_A6: IC1.16 (PA6); also elsewhere on the board
PORT_B0: IC1.18 (PB0); also elsewhere on the board
PORT_B1: IC1.19 (PB1); also elsewhere on the board
PORT_B2: IC1.20 (PB2); also elsewhere on the board
PORT_B3: IC1.39 (PB3); also elsewhere on the board
PORT_B4: IC1.40 (PB4); also elsewhere on the board
PORT_B5: IC1.41 (PB5); also elsewhere on the board
PORT_B6: IC1.42 (PB6); also elsewhere on the board
SWCLK: IC1.37 (PA14), X1.2
SWDIO: IC1.34 (PA13), X1.4
UART_RX: IC1.31 (PA10), X2.28
UART_TX: IC1.30 (PA9), IC2.2 (I), RN2.1

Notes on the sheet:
Licensed under the TAPR Open Hardware License (www.tapr.org/OHL)
Repository: https://github.com/eez-open
More info at http://www.envox.hr/eez
DIB, MCU, EEPROM, 3V3 LDO
Plastic parts
I2C Module ID EEPROM
+3V3 LDO
JTAG/SWD (optional)
DIB connector
ADIB connectors

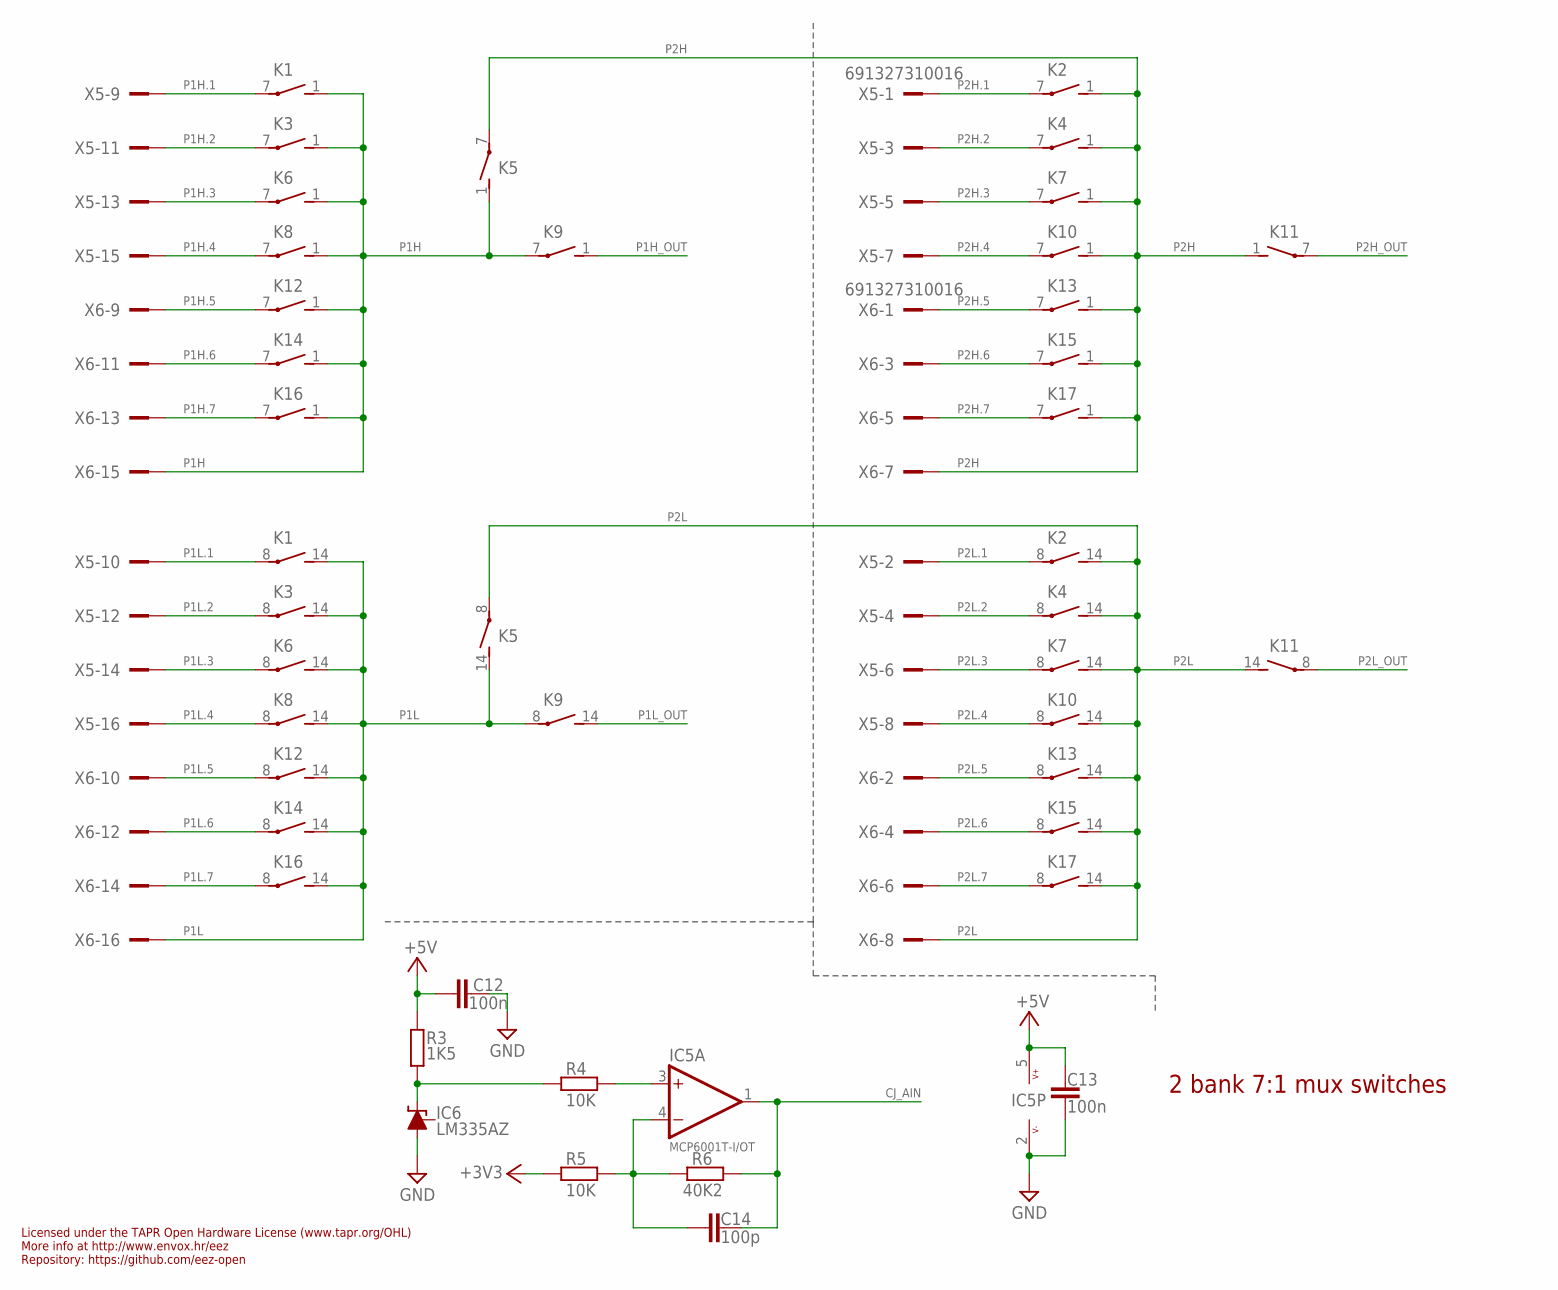
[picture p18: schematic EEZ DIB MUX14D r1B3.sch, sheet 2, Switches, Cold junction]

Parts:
C12, C13: 100n; C0603
C14: 100p; C0805
IC5: MCP6001T-I/OT; DBV5
IC6: LM335AZ; TO92
K1, K2, K3, K4, K6, K7, K8, K9, K10, K11, K12, K13, K14, K15, K16, K17: HE722A0500; RR2A
K5: HE721A0500; RR2A
R3: 1K5; R0805
R4, R5: 10K; R0805
R6: 40K2; R0805
X5, X6: 691327310016

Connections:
+3V3: R5.2; also elsewhere on the board
+5V: C12.1, C13.1, IC5.5 (V+), R3.1; also elsewhere on the board
CJ_AIN: C14.2, IC5.1 (OUT), R6.1; also elsewhere on the board
GND: C12.2, C13.2, IC5.2 (V-), IC6.3 (A); also elsewhere on the board
unnamed: IC6.2 (C), R3.2, R4.2
unnamed: C14.1, IC5.4 (-IN), R5.1, R6.2
unnamed: IC5.3 (+IN), R4.1
P1H: K1.1 (S), K3.1 (S), K5.1 (S), K6.1 (S), K8.1 (S), K9.7, K12.1 (S), K14.1 (S), K16.1 (S), X6.15
P1H.1: K1.7, X5.9
P1H.2: K3.7, X5.11
P1H.3: K6.7, X5.13
P1H.4: K8.7, X5.15
P1H.5: K12.7, X6.9
P1H.6: K14.7, X6.11
P1H.7: K16.7, X6.13
P1H_OUT: K9.1 (S); also elsewhere on the board
P1L: K1.14 (S), K3.14 (S), K5.14 (S), K6.14 (S), K8.14 (S), K9.8, K12.14 (S), K14.14 (S), K16.14 (S), X6.16
P1L.1: K1.8, X5.10
P1L.2: K3.8, X5.12
P1L.3: K6.8, X5.14
P1L.4: K8.8, X5.16
P1L.5: K12.8, X6.10
P1L.6: K14.8, X6.12
P1L.7: K16.8, X6.14
P1L_OUT: K9.14 (S); also elsewhere on the board
P2H: K2.1 (S), K4.1 (S), K5.7, K7.1 (S), K10.1 (S), K11.1 (S), K13.1 (S), K15.1 (S), K17.1 (S), X6.7
P2H.1: K2.7, X5.1
P2H.2: K4.7, X5.3
P2H.3: K7.7, X5.5
P2H.4: K10.7, X5.7
P2H.5: K13.7, X6.1
P2H.6: K15.7, X6.3
P2H.7: K17.7, X6.5
P2H_OUT: K11.7; also elsewhere on the board
P2L: K2.14 (S), K4.14 (S), K5.8, K7.14 (S), K10.14 (S), K11.14 (S), K13.14 (S), K15.14 (S), K17.14 (S), X6.8
P2L.1: K2.8, X5.2
P2L.2: K4.8, X5.4
P2L.3: K7.8, X5.6
P2L.4: K10.8, X5.8
P2L.5: K13.8, X6.2
P2L.6: K15.8, X6.4
P2L.7: K17.8, X6.6
P2L_OUT: K11.8; also elsewhere on the board

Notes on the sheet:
Licensed under the TAPR Open Hardware License (www.tapr.org/OHL)
Repository: https://github.com/eez-open
More info at http://www.envox.hr/eez
2 bank 7:1 mux switches

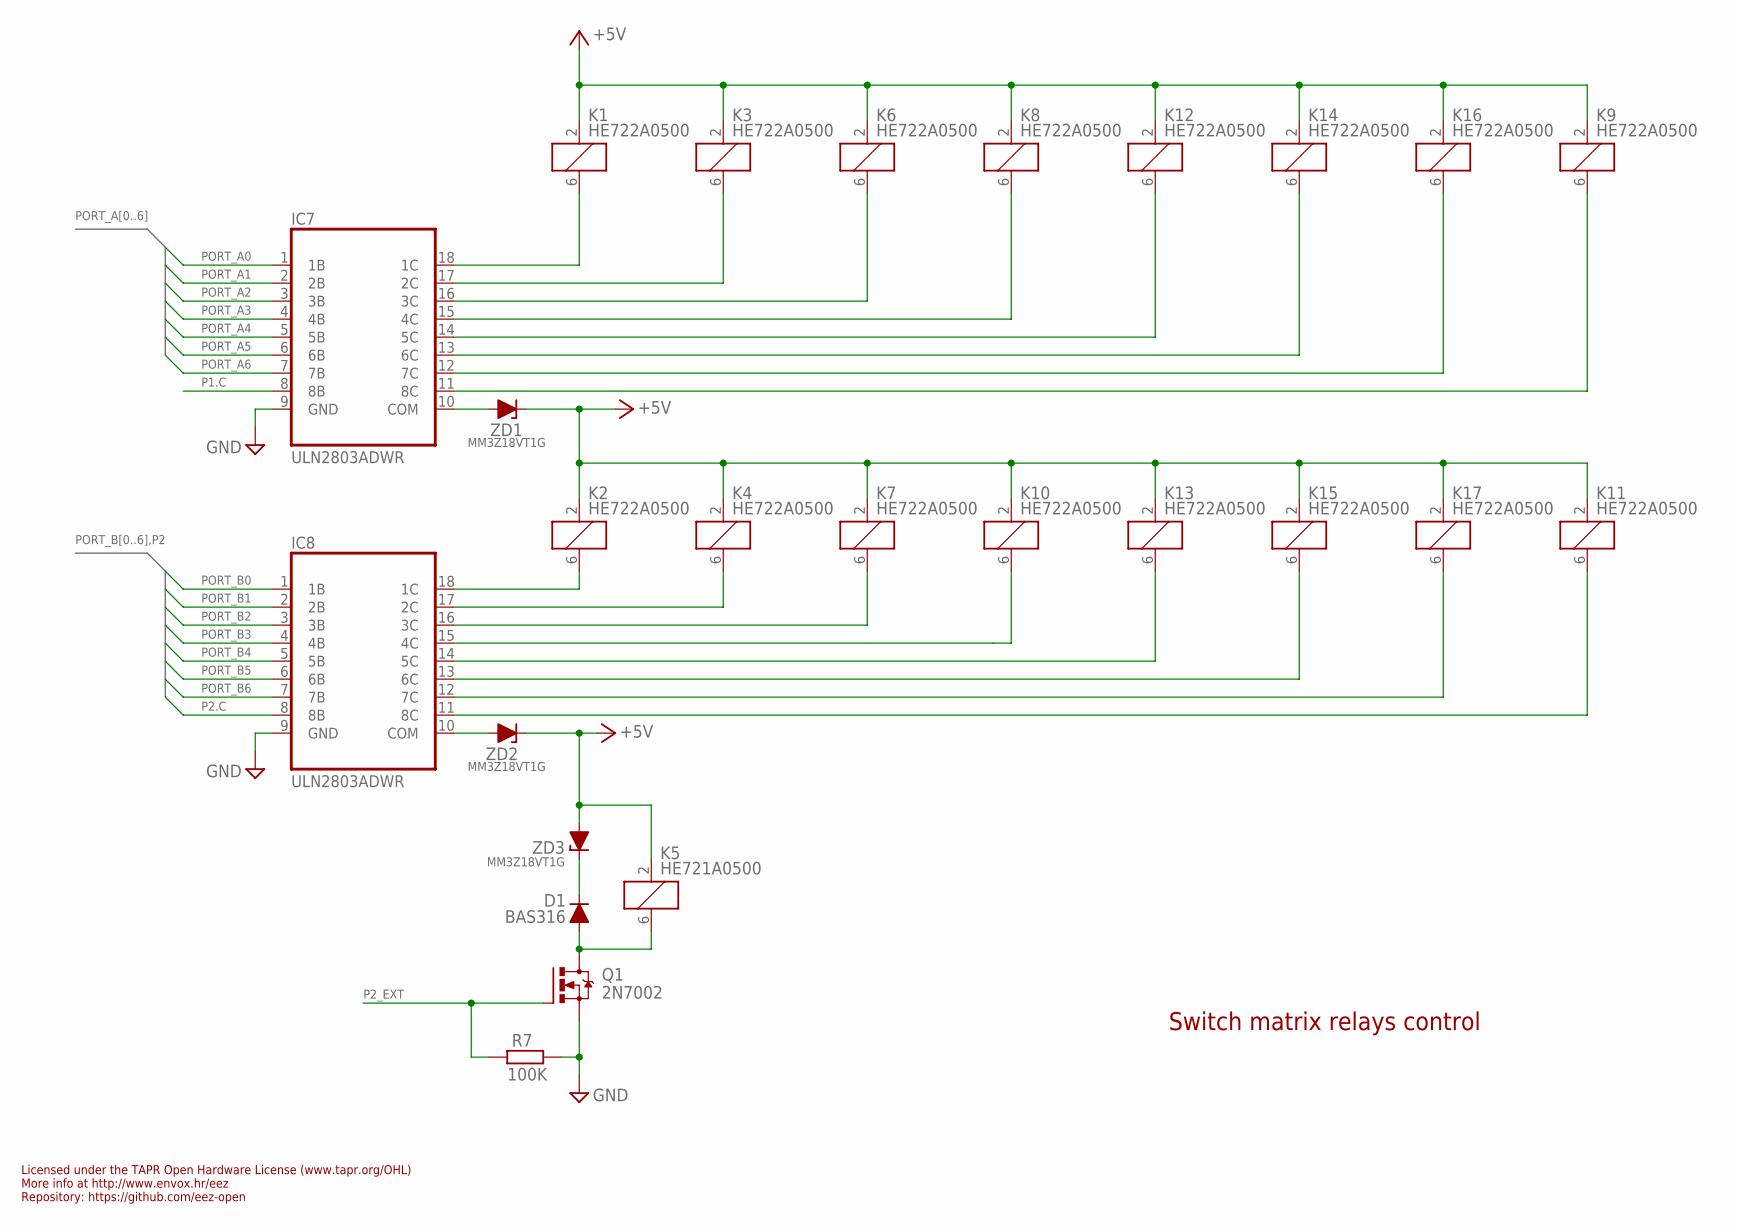
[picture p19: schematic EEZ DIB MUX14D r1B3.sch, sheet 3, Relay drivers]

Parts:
D1: BAS316; SOD323-R
IC7, IC8: ULN2803ADWR; DW18_TEX-M
K1, K2, K3, K4, K6, K7, K8, K9, K10, K11, K12, K13, K14, K15, K16, K17: HE722A0500; RR2A
K5: HE721A0500; RR2A
Q1: 2N7002; SOT103P240X110-3N; MPN 2N7002-7-F
R7: 100K; R0805
ZD1, ZD2, ZD3: MM3Z18VT1G; SOD323-R

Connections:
+5V: K1.2 (1), K2.2 (1), K3.2 (1), K4.2 (1), K5.2 (1), K6.2 (1), K7.2 (1), K8.2 (1), K9.2 (1), K10.2 (1), K11.2 (1), K12.2 (1), K13.2 (1), K14.2 (1), K15.2 (1), K16.2 (1), K17.2 (1), ZD1.C, ZD2.C, ZD3.A; also elsewhere on the board
GND: IC7.9 (GND), IC8.9 (GND), Q1.2 (S), R7.2; also elsewhere on the board
unnamed: D1.C, ZD3.C
unnamed: IC7.10 (COM), ZD1.A
unnamed: IC7.18 (1C), K1.6 (2)
unnamed: IC7.17 (2C), K3.6 (2)
unnamed: IC7.16 (3C), K6.6 (2)
unnamed: IC7.15 (4C), K8.6 (2)
unnamed: IC7.14 (5C), K12.6 (2)
unnamed: IC7.13 (6C), K14.6 (2)
unnamed: IC7.12 (7C), K16.6 (2)
unnamed: IC7.11 (8C), K9.6 (2)
unnamed: D1.A, K5.6 (2), Q1.3 (D)
unnamed: IC8.10 (COM), ZD2.A
unnamed: IC8.18 (1C), K2.6 (2)
unnamed: IC8.17 (2C), K4.6 (2)
unnamed: IC8.16 (3C), K7.6 (2)
unnamed: IC8.15 (4C), K10.6 (2)
unnamed: IC8.14 (5C), K13.6 (2)
unnamed: IC8.13 (6C), K15.6 (2)
unnamed: IC8.12 (7C), K17.6 (2)
unnamed: IC8.11 (8C), K11.6 (2)
P1.C: IC7.8 (8B); also elsewhere on the board
P2.C: IC8.8 (8B); also elsewhere on the board
P2_EXT: Q1.1 (G), R7.1; also elsewhere on the board
PORT_A0: IC7.1 (1B); also elsewhere on the board
PORT_A1: IC7.2 (2B); also elsewhere on the board
PORT_A2: IC7.3 (3B); also elsewhere on the board
PORT_A3: IC7.4 (4B); also elsewhere on the board
PORT_A4: IC7.5 (5B); also elsewhere on the board
PORT_A5: IC7.6 (6B); also elsewhere on the board
PORT_A6: IC7.7 (7B); also elsewhere on the board
PORT_B0: IC8.1 (1B); also elsewhere on the board
PORT_B1: IC8.2 (2B); also elsewhere on the board
PORT_B2: IC8.3 (3B); also elsewhere on the board
PORT_B3: IC8.4 (4B); also elsewhere on the board
PORT_B4: IC8.5 (5B); also elsewhere on the board
PORT_B5: IC8.6 (6B); also elsewhere on the board
PORT_B6: IC8.7 (7B); also elsewhere on the board

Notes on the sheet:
Licensed under the TAPR Open Hardware License (www.tapr.org/OHL)
Repository: https://github.com/eez-open
More info at http://www.envox.hr/eez
Switch matrix relays control

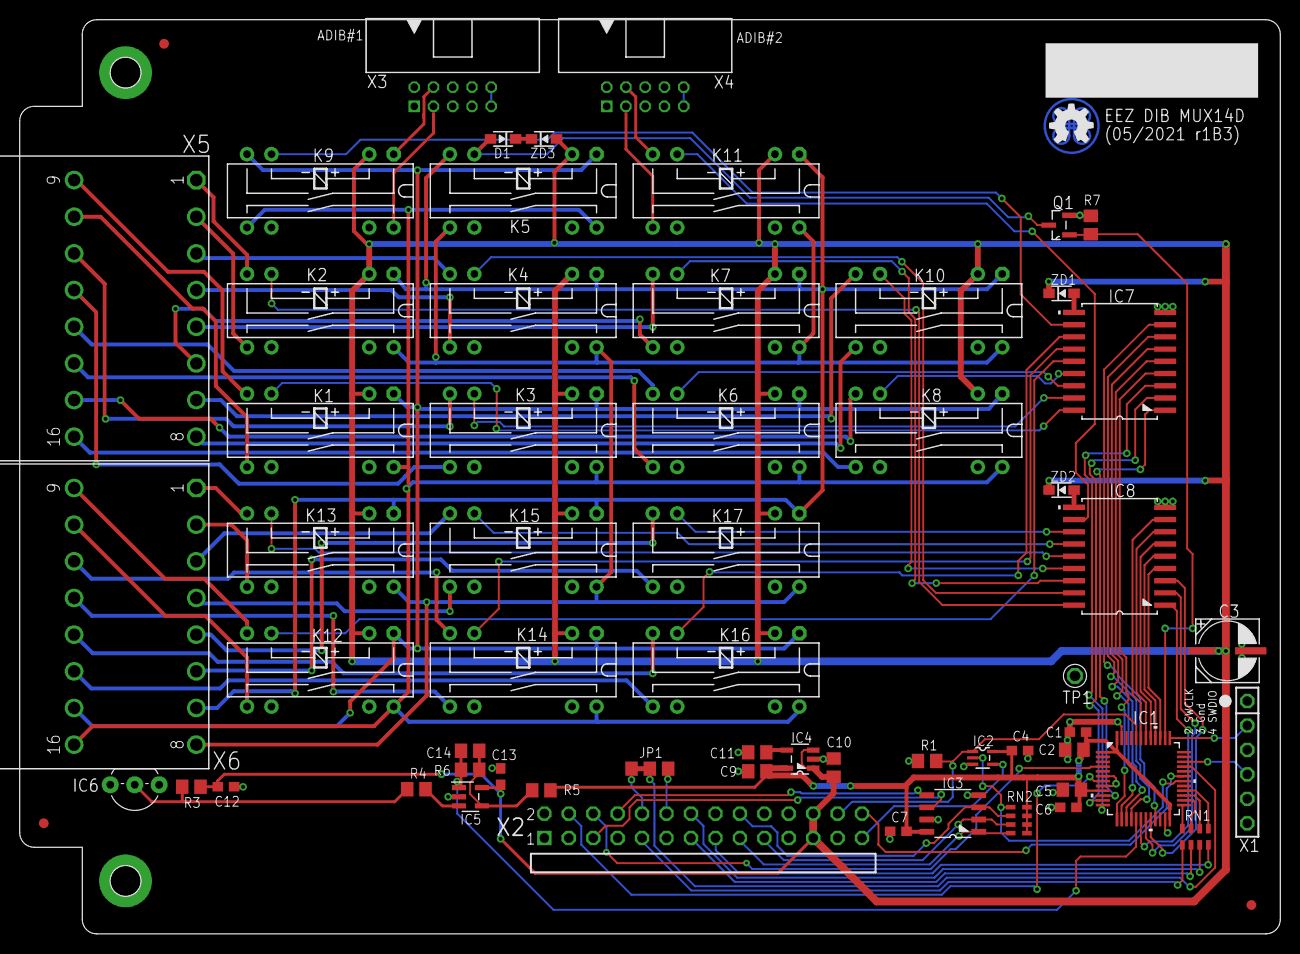
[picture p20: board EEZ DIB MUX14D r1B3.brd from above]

Board: 2 copper layers, 131.0 x 95.0 mm, 65 parts (0 on the bottom side), 107 nets.

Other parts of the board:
EEZ_SIGNATURE: SIGNATURESMALL; SIGNATURE_5MM

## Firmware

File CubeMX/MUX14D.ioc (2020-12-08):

#MicroXplorer Configuration settings - do not modify
Dma.Request0=SPI1_RX
Dma.Request1=SPI1_TX
Dma.RequestsNb=2
Dma.SPI1_RX.0.Direction=DMA_PERIPH_TO_MEMORY
Dma.SPI1_RX.0.Instance=DMA1_Channel2
Dma.SPI1_RX.0.MemDataAlignment=DMA_MDATAALIGN_BYTE
Dma.SPI1_RX.0.MemInc=DMA_MINC_ENABLE
Dma.SPI1_RX.0.Mode=DMA_NORMAL
Dma.SPI1_RX.0.PeriphDataAlignment=DMA_PDATAALIGN_BYTE
Dma.SPI1_RX.0.PeriphInc=DMA_PINC_DISABLE
Dma.SPI1_RX.0.Priority=DMA_PRIORITY_LOW
Dma.SPI1_RX.0.RequestParameters=Instance,Direction,PeriphInc,MemInc,PeriphDataAlignment,MemDataAlignment,Mode,Priority
Dma.SPI1_TX.1.Direction=DMA_MEMORY_TO_PERIPH
Dma.SPI1_TX.1.Instance=DMA1_Channel3
Dma.SPI1_TX.1.MemDataAlignment=DMA_MDATAALIGN_BYTE
Dma.SPI1_TX.1.MemInc=DMA_MINC_ENABLE
Dma.SPI1_TX.1.Mode=DMA_NORMAL
Dma.SPI1_TX.1.PeriphDataAlignment=DMA_PDATAALIGN_BYTE
Dma.SPI1_TX.1.PeriphInc=DMA_PINC_DISABLE
Dma.SPI1_TX.1.Priority=DMA_PRIORITY_LOW
Dma.SPI1_TX.1.RequestParameters=Instance,Direction,PeriphInc,MemInc,PeriphDataAlignment,MemDataAlignment,Mode,Priority
File.Version=6
GPIO.groupedBy=Group By Peripherals
KeepUserPlacement=false
Mcu.Family=STM32F0
Mcu.IP0=CRC
Mcu.IP1=DMA
Mcu.IP2=NVIC
Mcu.IP3=RCC
Mcu.IP4=SPI1
Mcu.IP5=SYS
Mcu.IP6=USART1
Mcu.IPNb=7
Mcu.Name=STM32F030C6Tx
Mcu.Package=LQFP48
Mcu.Pin0=PC15-OSC32_OUT
Mcu.Pin1=PA0
Mcu.Pin10=PB1
Mcu.Pin11=PB2
Mcu.Pin12=PB12
Mcu.Pin13=PB13
Mcu.Pin14=PB14
Mcu.Pin15=PB15
Mcu.Pin16=PA9
Mcu.Pin17=PA10
Mcu.Pin18=PA12
Mcu.Pin19=PA13
Mcu.Pin2=PA1
Mcu.Pin20=PA14
Mcu.Pin21=PA15
Mcu.Pin22=PB3
Mcu.Pin23=PB4
Mcu.Pin24=PB5
Mcu.Pin25=PB6
Mcu.Pin26=PB7
Mcu.Pin27=VP_CRC_VS_CRC
Mcu.Pin28=VP_SYS_VS_Systick
Mcu.Pin3=PA2
Mcu.Pin4=PA3
Mcu.Pin5=PA4
Mcu.Pin6=PA5
Mcu.Pin7=PA6
Mcu.Pin8=PA7
Mcu.Pin9=PB0
Mcu.PinsNb=29
Mcu.ThirdPartyNb=0
Mcu.UserConstants=
Mcu.UserName=STM32F030C6Tx
MxCube.Version=5.6.1
MxDb.Version=DB.5.0.60
NVIC.DMA1_Channel2_3_IRQn=true\:0\:0\:false\:false\:true\:false\:true
NVIC.ForceEnableDMAVector=true
NVIC.HardFault_IRQn=true\:0\:0\:false\:false\:true\:false\:false
NVIC.NonMaskableInt_IRQn=true\:0\:0\:false\:false\:true\:false\:false
NVIC.PendSV_IRQn=true\:0\:0\:false\:false\:true\:false\:false
NVIC.SVC_IRQn=true\:0\:0\:false\:false\:true\:false\:false
NVIC.SysTick_IRQn=true\:0\:0\:false\:false\:true\:false\:true
PA0.GPIOParameters=GPIO_Label
PA0.GPIO_Label=P1.0
PA0.Locked=true
PA0.Signal=GPIO_Output
PA1.GPIOParameters=GPIO_Label
PA1.GPIO_Label=P1.1
PA1.Locked=true
PA1.Signal=GPIO_Output
PA10.Locked=true
PA10.Mode=Asynchronous
PA10.Signal=USART1_RX
PA12.GPIOParameters=GPIO_Label
PA12.GPIO_Label=DIB_IRQ
PA12.Locked=true
PA12.Signal=GPIO_Output
PA13.Mode=Serial_Wire
PA13.Signal=SYS_SWDIO
PA14.Mode=Serial_Wire
PA14.Signal=SYS_SWCLK
PA15.GPIOParameters=GPIO_Label
PA15.GPIO_Label=P2_EXT
PA15.Locked=true
PA15.Signal=GPIO_Output
PA2.GPIOParameters=GPIO_Label
PA2.GPIO_Label=P1.2
PA2.Locked=true
PA2.Signal=GPIO_Output
PA3.GPIOParameters=GPIO_Label
PA3.GPIO_Label=P1.3
PA3.Locked=true
PA3.Signal=GPIO_Output
PA4.GPIOParameters=GPIO_Label
PA4.GPIO_Label=P1.4
PA4.Locked=true
PA4.Signal=GPIO_Output
PA5.GPIOParameters=GPIO_Label
PA5.GPIO_Label=P1.5
PA5.Locked=true
PA5.Signal=GPIO_Output
PA6.GPIOParameters=GPIO_Label
PA6.GPIO_Label=P1.6
PA6.Locked=true
PA6.Signal=GPIO_Output
PA7.GPIOParameters=GPIO_Label
PA7.GPIO_Label=P1.7
PA7.Locked=true
PA7.Signal=GPIO_Output
PA9.Locked=true
PA9.Mode=Asynchronous
PA9.Signal=USART1_TX
PB0.GPIOParameters=GPIO_Label
PB0.GPIO_Label=P2.0
PB0.Locked=true
PB0.Signal=GPIO_Output
PB1.GPIOParameters=GPIO_Label
PB1.GPIO_Label=P2.1
PB1.Locked=true
PB1.Signal=GPIO_Output
PB12.GPIOParameters=GPIO_Label
PB12.GPIO_Label=DIB_CSA
PB12.Mode=NSS_Signal_Hard_Input
PB12.Signal=SPI1_NSS
PB13.GPIOParameters=GPIO_Label
PB13.GPIO_Label=DIB_SCLK
PB13.Mode=Full_Duplex_Slave
PB13.Signal=SPI1_SCK
PB14.GPIOParameters=GPIO_Label
PB14.GPIO_Label=DIB_MISO
PB14.Mode=Full_Duplex_Slave
PB14.Signal=SPI1_MISO
PB15.GPIOParameters=GPIO_Label
PB15.GPIO_Label=DIB_MOSI
PB15.Mode=Full_Duplex_Slave
PB15.Signal=SPI1_MOSI
PB2.GPIOParameters=GPIO_Label
PB2.GPIO_Label=P2.2
PB2.Locked=true
PB2.Signal=GPIO_Output
PB3.GPIOParameters=GPIO_Label
PB3.GPIO_Label=P2.3
PB3.Locked=true
PB3.Signal=GPIO_Output
PB4.GPIOParameters=GPIO_Label
PB4.GPIO_Label=P2.4
PB4.Locked=true
PB4.Signal=GPIO_Output
PB5.GPIOParameters=GPIO_Label
PB5.GPIO_Label=P2.5
PB5.Locked=true
PB5.Signal=GPIO_Output
PB6.GPIOParameters=GPIO_Label
PB6.GPIO_Label=P2.6
PB6.Locked=true
PB6.Signal=GPIO_Output
PB7.GPIOParameters=GPIO_Label
PB7.GPIO_Label=P2.7
PB7.Locked=true
PB7.Signal=GPIO_Output
PC15-OSC32_OUT.GPIOParameters=GPIO_Label
PC15-OSC32_OUT.GPIO_Label=DIB_SYNC
PC15-OSC32_OUT.Locked=true
PC15-OSC32_OUT.Signal=GPIO_Input
PinOutPanel.RotationAngle=0
ProjectManager.AskForMigrate=true
ProjectManager.BackupPrevious=false
ProjectManager.CompilerOptimize=6
ProjectManager.ComputerToolchain=false
ProjectManager.CoupleFile=false
ProjectManager.CustomerFirmwarePackage=
ProjectManager.DefaultFWLocation=true
ProjectManager.DeletePrevious=true
ProjectManager.DeviceId=STM32F030C6Tx
ProjectManager.FirmwarePackage=STM32Cube FW_F0 V1.11.0
ProjectManager.FreePins=false
ProjectManager.HalAssertFull=false
ProjectManager.HeapSize=0x200
ProjectManager.KeepUserCode=true
ProjectManager.LastFirmware=false
ProjectManager.LibraryCopy=0
ProjectManager.MainLocation=Src
ProjectManager.NoMain=false
ProjectManager.PreviousToolchain=
ProjectManager.ProjectBuild=false
ProjectManager.ProjectFileName=MUX14D.ioc
ProjectManager.ProjectName=MUX14D
ProjectManager.StackSize=0x400
ProjectManager.TargetToolchain=EWARM V8.32
ProjectManager.ToolChainLocation=
ProjectManager.UnderRoot=false
ProjectManager.functionlistsort=
RCC.FamilyName=M
RCC.IPParameters=FamilyName,PLLCLKFreq_Value,PLLMCOFreq_Value,TimSysFreq_Value
RCC.PLLCLKFreq_Value=8000000
RCC.PLLMCOFreq_Value=8000000
RCC.TimSysFreq_Value=8000000
SPI1.Direction=SPI_DIRECTION_2LINES
SPI1.IPParameters=VirtualType,Mode,Direction,VirtualNSS
SPI1.Mode=SPI_MODE_SLAVE
SPI1.VirtualNSS=VM_NSSHARD
SPI1.VirtualType=VM_SLAVE
USART1.IPParameters=VirtualMode-Asynchronous
USART1.VirtualMode-Asynchronous=VM_ASYNC
VP_CRC_VS_CRC.Mode=CRC_Activate
VP_CRC_VS_CRC.Signal=CRC_VS_CRC
VP_SYS_VS_Systick.Mode=SysTick
VP_SYS_VS_Systick.Signal=SYS_VS_Systick
board=custom

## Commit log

2020-12-08 K9, K8, K17 rotated on PCB
    [EEZ DIB MUX14D r1B2.GBL, EEZ DIB MUX14D r1B2.GBO, EEZ DIB MUX14D r1B2.GBS, EEZ DIB MUX14D r1B2.GKO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]
2020-12-19 ADIB ID=002
    [EEZ DIB MUX14D r1B2.GBL, EEZ DIB MUX14D r1B2.brd, EEZ DIB MUX14D r1B2.sch]
2021-01-22 small PCB layout corrections
    [EEZ DIB MUX14D r1B2.GBL, EEZ DIB MUX14D r1B2.GBO, EEZ DIB MUX14D r1B2.GBS, EEZ DIB MUX14D r1B2.GTL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]
2021-01-30 PCB ID added
    [EEZ DIB MUX14D r1B2.GBL, EEZ DIB MUX14D r1B2.GTL, EEZ DIB MUX14D r1B2.brd, EEZ DIB MUX14D r1B2.sch]
2021-01-31 BOM update
    [EEZ DIB MUX14D r1B2 BOM.ods]
2021-03-28 Centroid files
    [EEZ DIB MUX14D r1B2 BOM.ods, EEZ DIB MUX14D r1B3 BOM.ods, EEZ DIB MUX14D r1B3.GBL, EEZ DIB MUX14D r1B3.GBO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]
2021-04-10 prototype image updated
2022-06-14 Reed relay replacement
    [EEZ DIB MUX14D r1B3 BOM.ods, EEZ DIB MUX14D r1B3.brd, EEZ DIB MUX14D r1B3.sch]
2022-07-01 Reed relay model correction
    [EEZ DIB MUX14D r1B3 BOM.ods]

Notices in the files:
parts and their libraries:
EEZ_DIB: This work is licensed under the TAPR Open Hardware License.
